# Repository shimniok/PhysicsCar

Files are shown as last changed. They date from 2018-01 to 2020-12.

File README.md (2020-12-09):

# PhysicsCar
A simple, low friction, 3-wheel car powered by mousetrap (or other stuff) for teaching physics concepts.

Created using FreeCAD. STL files are exported from FreeCAD.

 ## Parts

 ### List of 3d printed parts

 | File | Description | Print instructions |
 | --- | --- | --- |
 | clamp | Clamps pull rod onto mousetrap | Print, cut apart in the middle for two halves |
 | crossmember | middle crossmember for front and rear frame dowels | Print 1x |
 | crossmember_front | narrow crossmember for front part of frame | Print 1x |
 | crossmember_rear | (optional) narrow crossmember for rear part of frame | Print 1x |
 | drive_flange | attaches each side of drive wheel | Print 2x |
 | drive_wheel | a wider wheel for stability and traction | Print 1x |
 | hub | holds axles/wheels in place | Print 4x |
 | pull_end | add to end of pull rod, has loop to tie fishing wire | Print 1x
 | rod_end | slips on to frame ends, with hole for axle | Print 4x with full support |
 | trap mount | Mounts the mousetrap offset in the frame to center pull rod | see below |
 | trap_mount_A | Mounts the mousetrap on the front of the frame | Print 1x |
 | trap_mount_B | Mounts the mousetrap on the rear of the frame | Print 1x |
 | wheel | Low friction, low mass rear wheels | Print 2x |

### Additional parts

In addition to the following 3d printed parts, you'll need:

 * (4) 4.8mm x 30cm (3/16" x 11-7/8") wood dowels
 * (1) 1.95mm x 915mm (0.078" x 36") piano wire
 * (8) #6 x 1/2" wood screws
 * (2) #6 x 1" machine screws
 * (2) #6 machine nuts (nylock or use Loctite blue)
 * (1) length of fishing wire, >= 6lb test
 * (1) standard mousetrap e.g., Victor

## Assembly

### Tools needed
 * Safety goggles
 * Ear plugs if using power tools
 * Something to cut steel piano wire - Dremel with cutoff wheel, file to nick and pliers
 to bend back and forth and break
 * Screwdriver(s) for #6 hardware
 * Wrench for #6 nuts
 * Knife or scissors to cut clamp apart

### Frame
 * Push two rods into front crossmember about halfway.
 * Push other end of these two rods into the inner holes of the middle crossmember just
enough so their ends are flush with the other side of the crossmember.
 * Push two new rods into the outer holes of the middle crossmember just enough so their
ends are flush with the other side of the crossmember.
 * Push front trap mount onto rear rods
 * Insert trap into front trap mount so, when sprung, arm is to the rear.
 * Push rear trap mount onto rear rods and push onto rear of trap
 * Push rear crossmember onto rods a few inches
 * Push the rod ends onto ends of each rod

### Wheels
 * Insert wire, which will become rear axle, into rear rod end holes
 * Push rear wheels, hub inboard, onto each axle end
 * Push hub onto each end of the axle. Adjust for stable, low friction spin
 * Trim axle length
 * Use #6 wood screws to attach drive flanges to drive wheel
 * Hold drive wheel/flanges in between front rod ends
 * Push another wire through one rod end, through drive wheel, and through other rod end.
 * Push hub onto each end of the axle. Adjust for stable, low friction spin
 * Trim axle length

### Pull rod
 * Cut clamp tab off, separating each half of the clamp
 * Use the #6 machine screws and nuts to loosely attach clamp onto the mouse trap arm
 * Insert pull rod into clamp
 * Insert pull rod end onto end of pull rod
 * Tie fishing wire onto pull rod end with a strong knot that won't pull loose
 * Attach fishing line to drive flange.
 * Rotate drive wheel to spool up fishing line and hold it to keep from rotating
 * Place on ground, release drive wheel, and zoom! :)

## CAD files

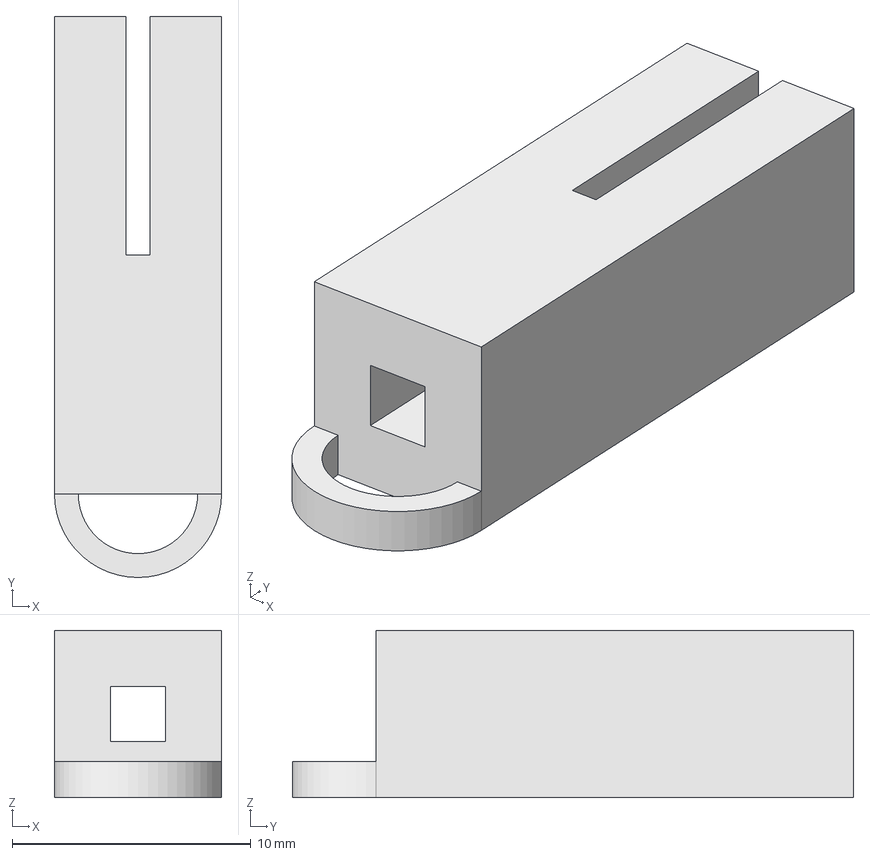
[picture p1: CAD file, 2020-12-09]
pull_end.fcstd
7.00 x 23.5 x 7.00 mm

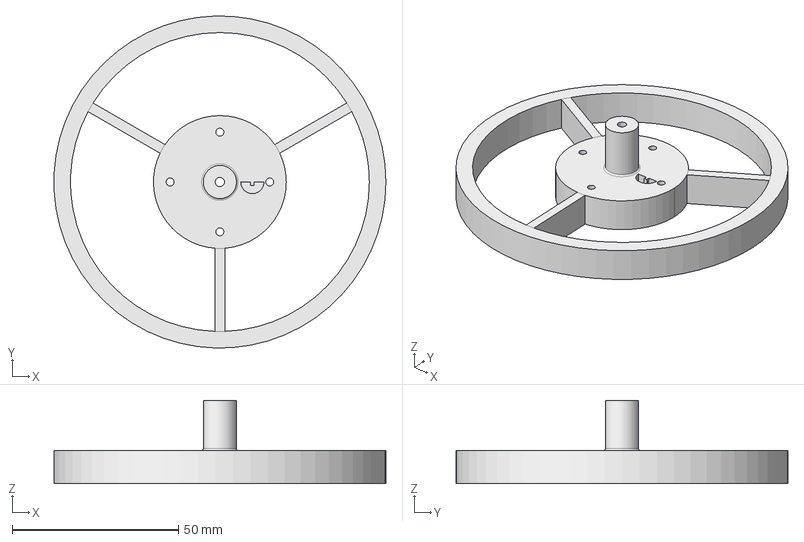
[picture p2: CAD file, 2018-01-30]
drive_wheel.fcstd
99.9 x 100.0 x 25.0 mm

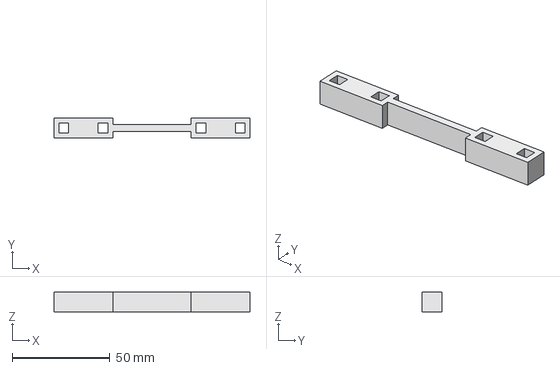
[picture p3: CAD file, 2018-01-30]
crossmember.fcstd
100.0 x 10.0 x 10.0 mm

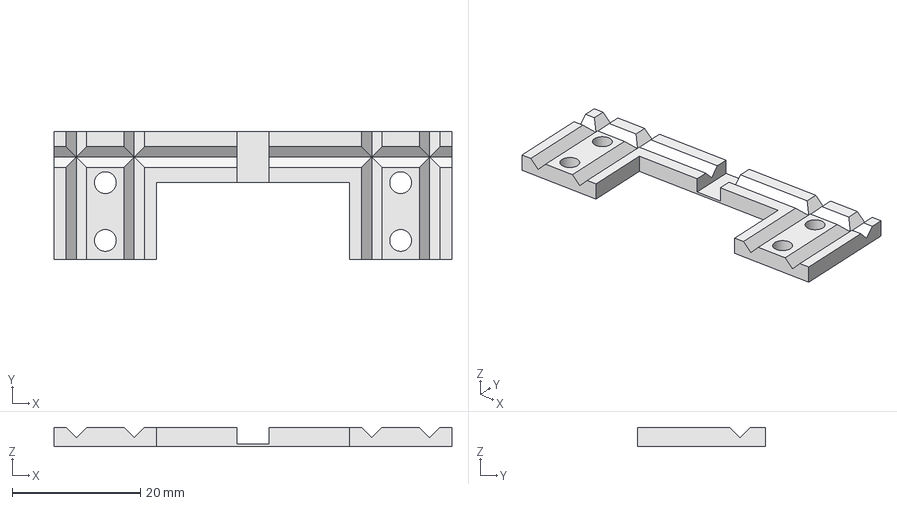
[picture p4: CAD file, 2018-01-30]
clamp.fcstd
62.0 x 20.0 x 3.00 mm

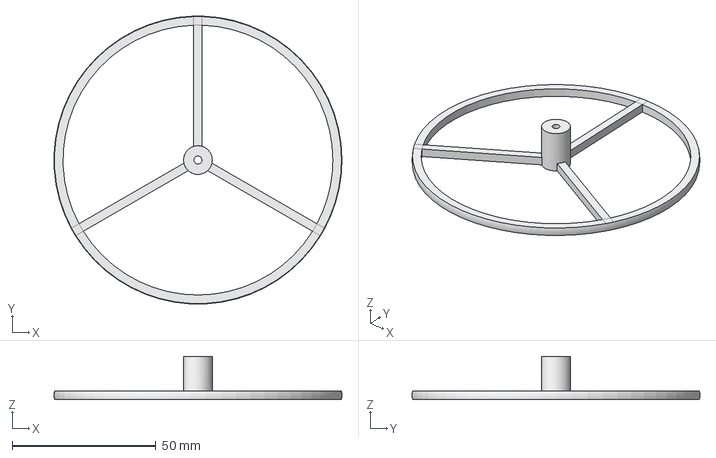
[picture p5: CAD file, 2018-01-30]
wheel.fcstd
100.3 x 100.3 x 15.0 mm

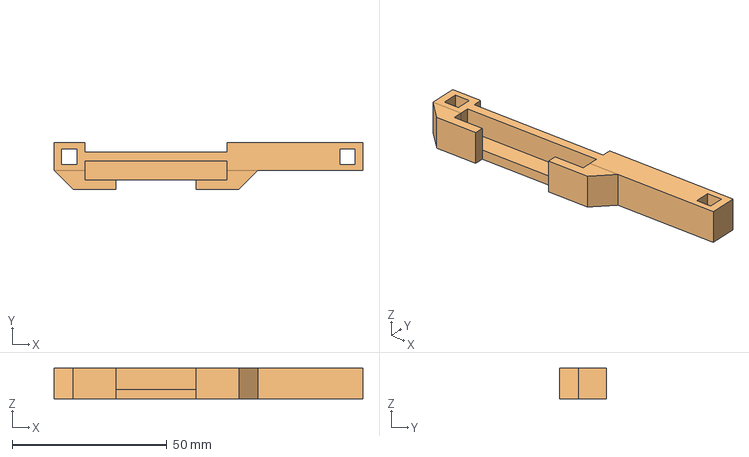
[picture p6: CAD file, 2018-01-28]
trap_mount.fcstd
100.0 x 15.1 x 10.0 mm

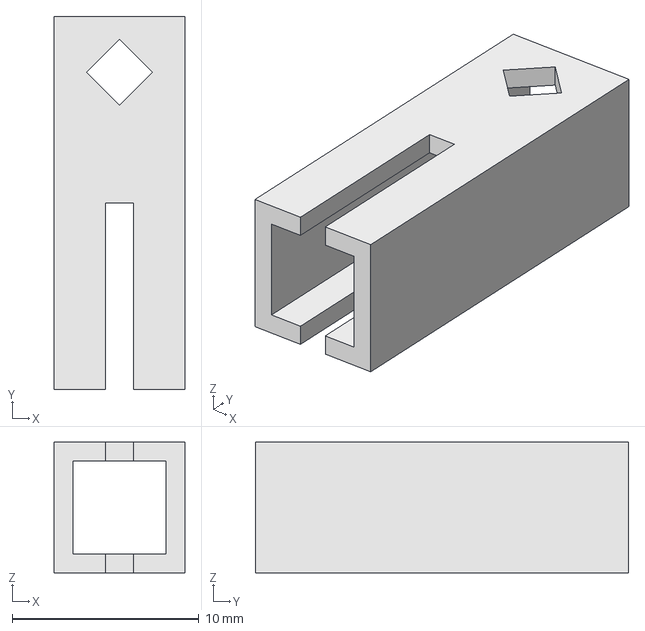
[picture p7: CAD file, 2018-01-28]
rod_end.fcstd
7.00 x 20.0 x 7.00 mm

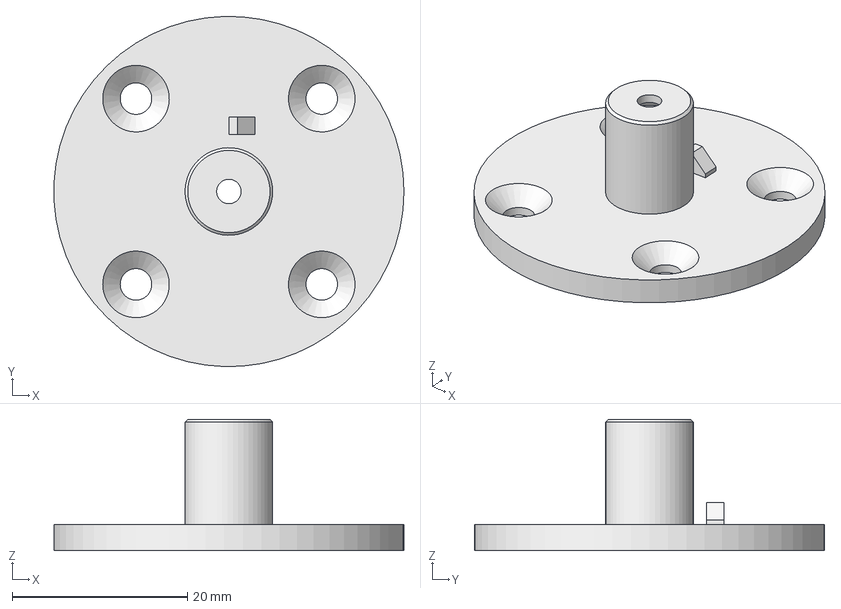
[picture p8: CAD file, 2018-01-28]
drive_flange.fcstd
40.0 x 40.0 x 15.0 mm

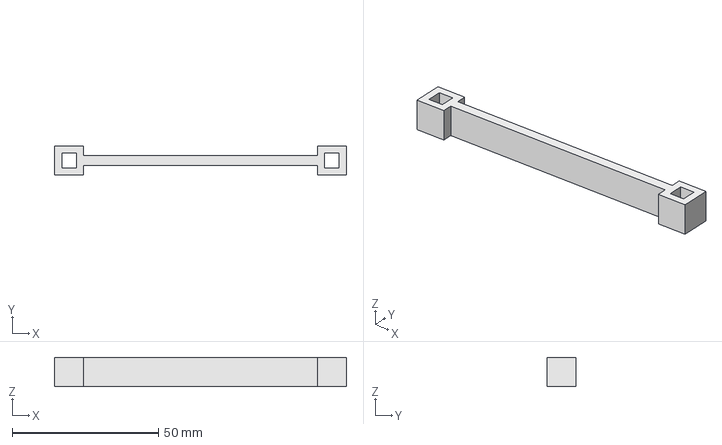
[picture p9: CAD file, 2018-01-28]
crossmember_rear.fcstd
100.0 x 10.0 x 10.0 mm

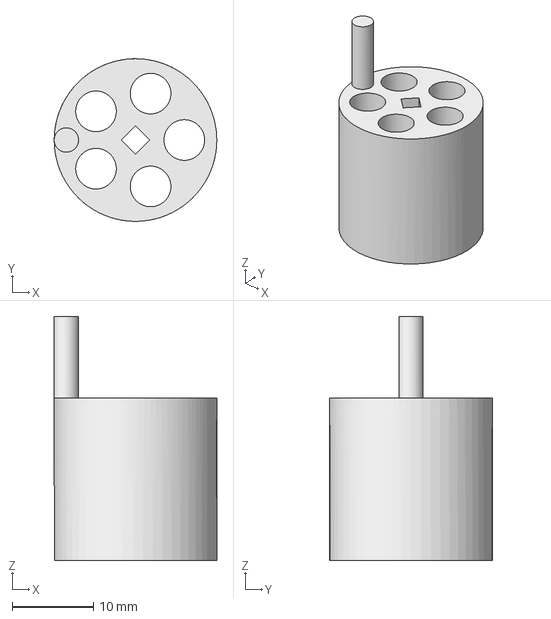
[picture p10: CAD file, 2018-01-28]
drive_spool.fcstd
20.0 x 20.0 x 30.0 mm

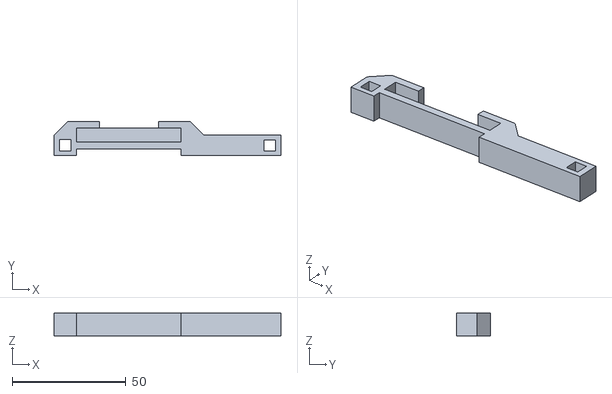
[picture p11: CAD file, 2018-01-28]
trap_mount_B.stl
100.0 x 15.1 x 10.0

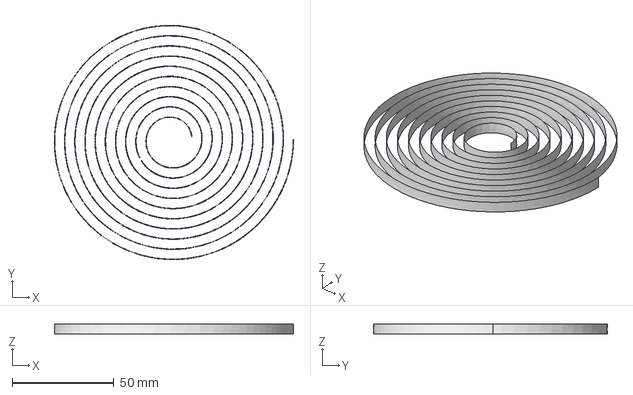
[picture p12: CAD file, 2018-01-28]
spiral.fcstd
117.5 x 115.0 x 5.00 mm

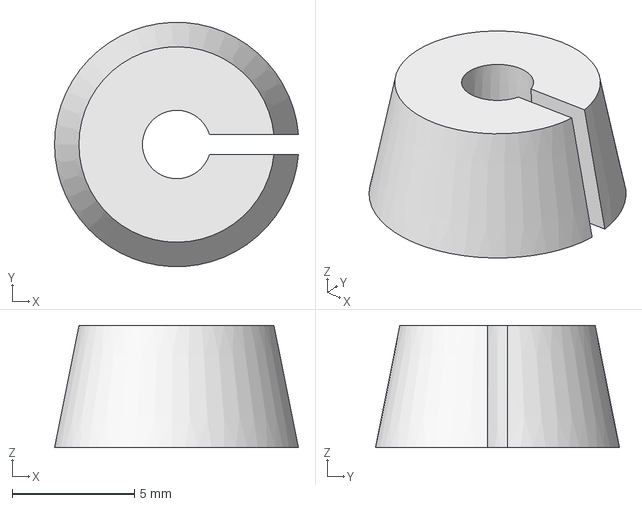
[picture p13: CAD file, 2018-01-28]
hub.fcstd
9.98 x 9.99 x 5.00 mm

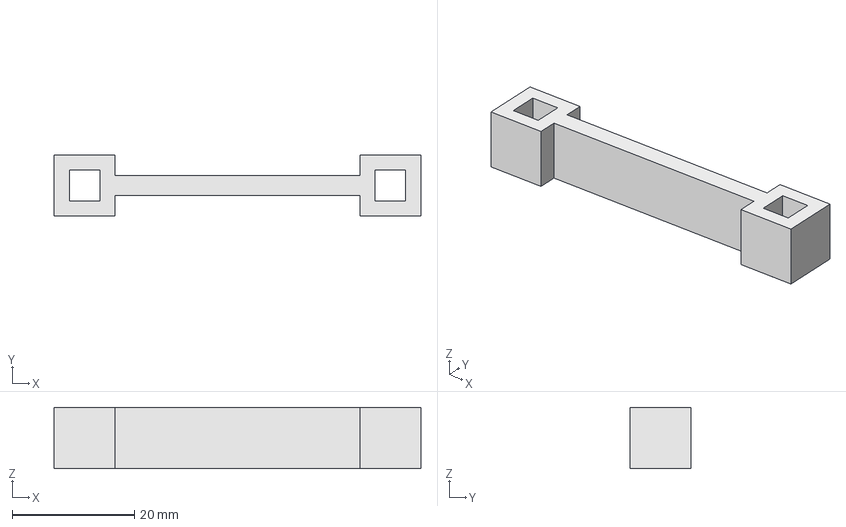
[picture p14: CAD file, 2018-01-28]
crossmember_front.fcstd
60.0 x 10.0 x 10.0 mm

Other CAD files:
drive_hub.fcstd
trap_mount_A.stl
drive_washer.fcstd
clamp.stl
crossmember.stl
crossmember_front.stl
crossmember_rear.stl
drive_flange.stl
drive_spool.stl
drive_washer.stl
drive_wheel.stl
hub.stl
pull_end.stl
rod_end.stl
trap_mount.stl
wheel.stl

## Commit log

2018-01-28 initial version
    [clamp.fcstd, clamp.stl, crossmember.fcstd, crossmember.stl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]
2018-01-28 renamed front* to rod_end*
    [rod_end.fcstd, rod_end.stl]
2018-01-28 Added print instructions to README
2018-01-30 Centered crossmember on build platform
    [crossmember.stl]
2018-01-30 replaced old wheel with new
    [wheel2.fcstd]
2018-01-30 fixed wheel diameter
    [wheel.fcstd, wheel.stl]
2018-01-30 updated clamp stl file
    [clamp.stl]
2018-01-30 updated clamp for symmetry
    [clamp.fcstd]
2018-01-30 Minor updates
    [crossmember.fcstd]
2018-01-30 Incorporated extended flange on one side, increased inner diameter
    [drive_wheel.fcstd]
2018-01-30 Fixed hub length (was short by 3mm)
    [clamp.stl, drive_wheel.fcstd, drive_wheel.stl]
2020-12-09 Added pull end object
    [pull_end.fcstd, pull_end.stl]
2020-12-09 Update README.md
    Updated trap mount, clamp; added pull end.
2020-12-09 Update README.md
    Updated trap mount.
2020-12-09 Updated readme with assembly instructions
